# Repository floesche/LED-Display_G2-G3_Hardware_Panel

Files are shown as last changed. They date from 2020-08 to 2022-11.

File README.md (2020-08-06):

---
title: Hardware
parent: Generation 2
---

This repository is related to the Panels project.  It includes the PCB design files, BOM, and datasheets for the (Gen-2) 8x8 LED Panels.

## Project content

```
├── fab_v1p3
└── pcb
    ├── datasheets
    ├── gerber_v1p0
    ├── gerber_v1p1
    ├── gerber_v1p2
    ├── gerber_v1p3
    ├── libs
    ├── mods
    └── old_bom
```

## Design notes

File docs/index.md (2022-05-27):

---
title: Panel
parent: Generation 2
nav_order: 3
---

# Panel 8x8 32mm

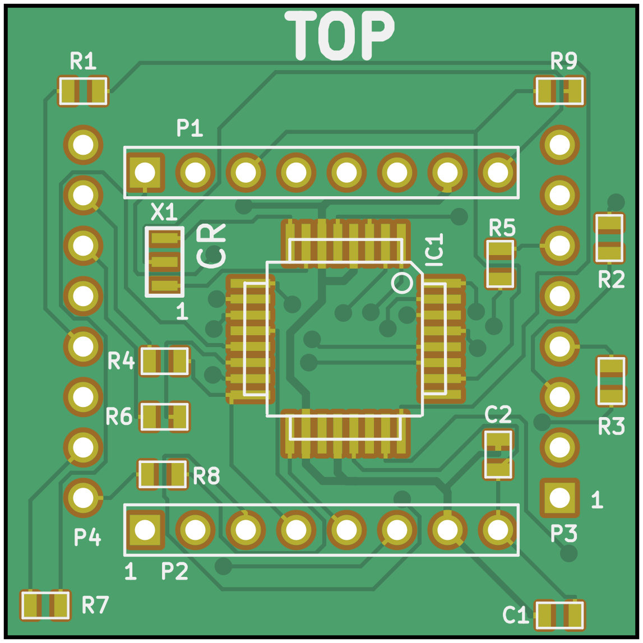
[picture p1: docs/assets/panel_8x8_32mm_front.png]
Panel PCB front view

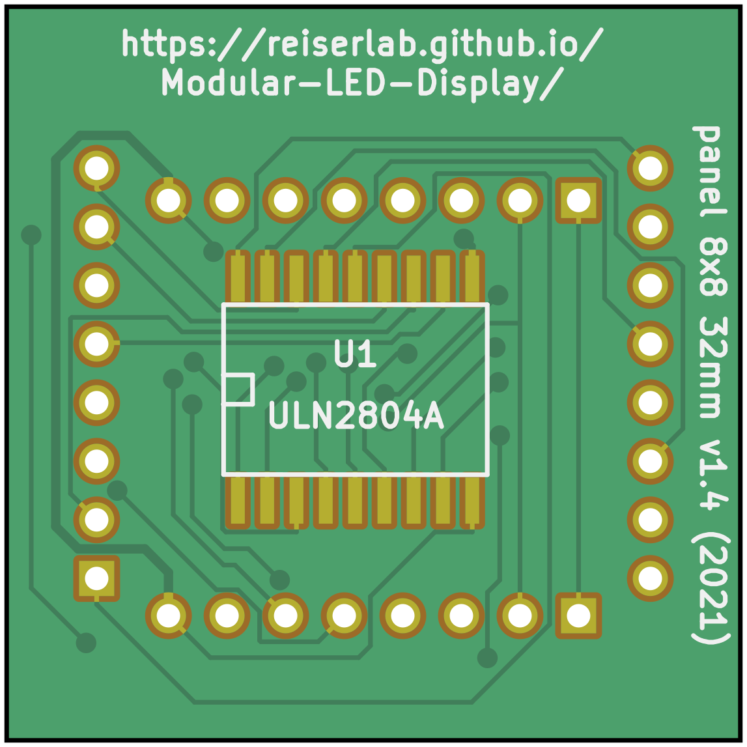
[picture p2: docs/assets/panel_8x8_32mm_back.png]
Panel PCB back view


The display devices in [Generation 2 (G2)]({{site.baseurl}}/G2/) and [Generation 3 (G3)]({{site.baseurl}}/G3/) of the Modular LED Display consists of a standard 8×8 LED matrix component mounted to a custom PCB. This custom PCB, in the original [paper](https://doi.org/10.1016/j.jneumeth.2007.07.019) and our [documentation]({{site.baseurl}}) referred to as the __panel__, is responsible for the communication with the controller. Each panel is individually addressed and communicates with the controller over the TWI bus. Each panel runs a small program which receives updated pattern information and refreshes the display.

__Note__: To clarify the terminology: in [Generation 4]({{site.baseurl}}/G4/) of the Modular LED Display, we built our own LED PCBs (then referred to as [_driver_]({{site.baseurl}}/Generation%204/Panel/docs/driver.html)), and the PCBs providing part of the panel board functionally being called [_comm board_]({{site.baseurl}}/Generation%204/Hardware/docs/comm.html).

## Components

The display devices are a small package that contains a panel board with a microprocessor and line driver, and an 8×8 LED dot matrix display. A brief overview of a [parts list](#parts-list) and the initial sketch of the [schematics](assets/panel_schematic_v2p1.pdf) and [board layout](assets/panel_pcb_v2p1.pdf) are archived here, but when in question always refer to the design and production files as they are more up to date. Each Panel contains an Atmel ATmega8 microcontroller. If you plan to program the Atmel chip, it is a good idea to read the ATmega8 spec sheet. The other chip on the circuit board is an 8-channel darlington driver which acts as a current sink. Current is sourced from the ATmega8's outputs and then passes through a current limiting resistor and one column of the 8×8 LED display. An individual LED is turned on only if the corresponding row line is enabled on the 8-channel current sink, allowing current to flow. In this way it is possible to scan the entire 8×8 array and thus 64 LEDs can be individually controlled with 16 lines. Of course, for this to happen no more than 1 row of LEDs can actually be on at any one time, and so the LEDs must be scanned quickly to prevent the perception of flicker. Currently the entire display is refreshed at 4kHz, and every LED that is on, is only on 12.5% of the time.

The LED matrix component [BM-10288MD](assets/datasheets/BM-10288MD.pdf) (or the alternative [BL-M12A811](assets/datasheets/BL-M12A881.pdf)) that was used in the Generation 2 displays measures 32×32mm² and consists of 8×8 = 64 LEDs. The panel board has the same dimension and is attached to the back of the matrix component. It contains an ATmega168-A and a ULN2804A to drive the LED matrix.

## Design and Production

The KiCad design files are in the `panel_8x8_32mm` directory. Gerber files and a Bill of Materials (BOM) are in a subdirectory `production_v1`. Data sheets for the components used in the built are archived in the `datasheets` directory. For historic reason and although completely outdated we also share the initial [cost estimation](assets/panel_8x8_32mm_costs.xls) done in 2011.

The most recent production of panels we are aware of was in 2020 (please [let us know]({{site.baseurl}}/Contact) if you built another batch). The [Frye lab](https://sites.lifesci.ucla.edu/ibp-frye/research/) used our files version 1.3 (generated in 2012) to order at [Bittele Electronics Inc](https://7pcb.com) in Canada. If you want to replicate the exact same order, feel free to include the order reference number Q12295E in your conversation with Bittele. The panels look a little different from the images above and used the name __flypanel__ internally. The exact same files used in this order are archived at `panel_8x8_32mm/production_v1/panel_8x8_32mm_v1p3.zip`.

The `panel_8x8_32mm/production_v1/panel_8x8_32mm_v1p4.zip` contains a more current, but untested update to the panel. If you are brave enough to order them and have experiences with it, then please get it [contact]({{site.baseurl}}/Contact).

## Software

__Note__: The following sections are out of date. Unless you need to repair a Generation 2 system, follow the instruction in the [Generation 3]({{site.baseurl}}/G3/) menu.
{:.warning}

The software running on each Panel's ATmega8 microcontroller is written in C code, and compiled using the GCC tools for the AVR (WinAVR distribution). Packets are sent to each panel over the TWI bus, the TWI unit on the ATmega8 will only accept a packet if it is addressed either with a 0 (general call) or the address of the panel. In this way specific panels can be targeted. The EEPROM of the ATmega8 is loaded with some patterns, so that the SRAM on the chip is available for pattern buffers. The EEPROM contains the character library for 0…9 and the patterns for the error codes. The EEPROM also has one byte designated for the panel ID, this is set to 0 during the programming.

### Support for Gray Scale (Green Scale)

Multiple levels of //greenscale// patterns are supported by the panels. This is accomplished by further dividing the 4kHz refresh of the panels into either 3 or 7 pieces. When divided into 3 time segments, 4 greenscale levels are possible -- that is each LED can be on for 0, 1, 2, or 3 of the 3 possible time slices. Similarly, when divided into 7 time segments, 8 greenscale levels are possible - each LED can be on for 0,1,…,7 of the 7 total time slices. When measured with a photometer, this scheme is remarkably linear, e.g. the luminance measured for greenlevel 6 is almost exactly 3 times the luminance measured for greenlevel 2. This does reduce the minimum refresh rate to about 570Hz for the 7 levels (so-called `Gray_Scale = 7`), and to about 1333Hz for the 3 levels (so-called `Gray_Scale = 3`). The simplest implementation of this would use 7 copies of the 64-bit pattern map, each bit specifying whether each LED should be on during each time slice. However, we take advantage of binary decoding -- so we need twice the bits -- 16 bytes for each pattern frame at `Gray_Scale = 3`, and 24 bytes for each panels piece of a `Gray_Scale = 7` pattern. The actual way this is done is just a lot of messy, uninteresting boolean algebra. Please read the code if you are interested.

### Panel Address

The address of each panel can be any integer from 1…127. The 0 address is reserved for a general call -- all panels receive packets sent to address 0. The address displays when the panels turn on (and after a reset). Also immediately after a rest or power on, the panels enter a 0.5 second pause, and will be unresponsive to commands and patterns. Only two characters are shown (00…99), and if the value is above 100, the top row of the panel is also  illuminated. It is necessary to give the panels addresses in an incremental manner. If 5 panels, all with address 0 are connected to the controller, and a change address command is issued, all panels with the same address will respond. Read the user guide for instructions on addressing panels.

## Programming the Panels

Because each panel has a microprocessor on-board, each panel needs to be programmed individually. The programming interface (or ISP, in system programming) lines only connect to the microprocessor when the panel is in the left-most position of the controller board, or the plug on the case-mount portion of the controller PCB. The procedure described here is for programming G2 panels (the fuse setting are different for G3 panels). In some eventual future, programming will be done directly from the MATLAB interface. As of right now the procedure is as follows:

1. Once the panel is in place, connect the programming device to the 6 pin header, labelled __Panel ISP__.
2. Open AVR Studio and start the AVR programming tool _STK500/AVRISP_{:.gui-btn} from the tools menu.
3. Test the connection by selecting the ATmega8 device from the drop-down menu, and then in the advanced tab try to read signature. If these match, move on, otherwise check the connections, restart, etc.
4. Program the fuses. This is done from the _Fuses_{:.gui-btn} tab – these options should be set: _Preserve EEPROM memory through chip erase cycle_{:.gui-txt} to _on_{:.gui-txt}, and set clock rate to the last choice: _Ext. Crystal/Resonator High Freq._{:.gui-txt}: _Start-up time 16K CK + 64 ms_{:.gui-txt}. It is also a good idea to set _Brown-out detection level at VCC_{:.gui-txt} = _4.0V_{:.gui-txt} and _Brown-out detection enabled_{:.gui-txt}.
5. Program the EEPROM on the Atmega8 by selecting the _Program_{:.gui-btn} tab and electing the input hex file as: _panel.eep_{:.gui-txt}, and then programming the chip.
6. Program the flash on the Atmega8 by selecting the _Program_{:.gui-btn} tab and selecting the input hex file as: _panel.hex_{:.gui-txt}, and then programming the chip.
7. If this is all done correctly the LED should display 00 and the display should be bright with no flicker. If it appears dull or flickery - the clock was probably not set correctly. It is always a good idea to verify both the program and the fuses to make sure these are set correctly.

For programming many panels this process can be automated by using the _Auto_{:.gui-btn} tab and selecting _program FLASH_{:.gui-txt}, _program EEPROM_{:.gui-txt}, and _program fuses_{:.gui-txt}. Once a panel is programmed it needs to be addressed, this is done using the PControl software.

# Parts list {#parts-list}

| quantity | part description               | source & p/n | price |
|---------:|:-------------------------------|:-------------|------:|
| 1        | 8×8 green [LED display]({{site.baseurl}}/Generation%203/Hardware/docs/assets/green-panels_BM-10288MD.pdf) | American Bright, BM-10288MI | $2.50 |
| 1        | 8 Pin rt angle male header              | Major League, LTSHR-108-S-02-A-T | $0.23 |
| 1        | 8 Pin rt angle fem. header              | Major League, SSHR-108-S-02-L-T | $0.38 |
| 8        | 82Ohm resistor, 1/10W, 1%, 0603 package | Digi-Key, 311-82.0HTR-ND | $0.005 |
| 1        | 1kOhm resistor, 1/10W, 5%, 0603 package | Digi-Key, 311-10KGCT-ND | $0.02 |
| 1        | 0.33µF capacitor, ceramic, 1206 package | Digi-Key, PCC1889CT-ND | $0.09 |
| 1        | 16MHz ceramic resonator w. capacitors   | Digi-Key, X908-ND | $0.30 |
| 1        | 8 CH line driver ULN2804A 8-SOL package | Digi-Key, ULN2804AFW-ND | $0.35 |
| 1        | [Atmega8](http://www.atmel.com/dyn/resources/prod_documents/doc2486.pdf) microcontroller, 32 TQFP package| Digi-Key, ATMEGA8-16AI-ND | $2.25 |
| 1        | Panel PCB                               | ordered from Advanced Circuits | |

__Optional__: 2 8-Pin straight female headers, Jameco p/n 70754 ($0.23), can be used so that the LED displays are socketed, this is convenient, but also will not guarantee ideal contact between circuit and display.

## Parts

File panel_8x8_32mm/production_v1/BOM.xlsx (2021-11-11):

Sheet: Sheet1
Item# | Qty | References | part desc. | mfg P/N | vendor | price | $100 | $500 | $1000 | $1500 | $2000 | 100 | 500 | 1000 | 1500 | 2000 | price/board_100 | price/board_500 | price/board_1000 | price/board_1500 | price/board_2000 | MOQ | Availability | Comments_Lj | Your Comments
1 | 1 | U1 | IC DRIVER DARL 8CH 50V.5A 18-SO | ULN2804AFWG(CELHACT-ND) | Digikey | 0.92 | 0.63 | 0.462 | 0.3675 | 0.336 | 0.3045 | 100 | 500 | 1000 | 1500 | 2000 | 0.63 | 0.462 | 0.3675 | 0.336 | 0.3045 | 1 | 26688
2 | 1 | IC1 | IC AVR MCU 16K 20MHZ 32TQFP | ATMEGA168-20AU-ND | Digikey | 4.32 | 2.412 | 2.412 | 2.412 | 2.412 | 2.412 | 100 | 500 | 1000 | 1500 | 2000 | 2.412 | 2.412 | 2.412 | 2.412 | 2.412 | 1 | 53937
3 | 2 | P3, P4 | 8 POS PEEL-A-WAY SIP CONN. | Custom | Adv. Interconn. |  |  |  |  |  |  |  |  |  | 3000 | 4000 | 0 | 0 | 0 | 0 | 0 |  |  |  | Already purchased. This is a 32 position strip. The board requires 2x8 pos strips.
4 | 8 | R1, R2, R3, R4, R5, R6, R7, R8 | RES 0603 82 OHM 1/10W 1% | P82.0HCT-ND | Digikey | 0.8 | 0.0105 | 0.00576 | 0.00384 | 0.00198 | 0.00198 | 800 | 4000 | 8000 | 12000 | 16000 | 0.084 | 0.04608 | 0.03072 | 0.01584 | 0.01584 | 1 | 77007
5 | 1 | R9 | RES 0603 10K OHM 1/10W 5% | P10KGCT-ND | Digikey | 0.1 | 0.007 | 0.00384 | 0.00256 | 0.00256 | 0.00256 | 100 | 500 | 1000 | 1500 | 2000 | 0.007 | 0.00384 | 0.00256 | 0.00256 | 0.00256 | 1 | 13551465
6 | 2 | C1, C2 | CAP 0603 0.33 uF | PCC2274CT-ND | Digikey | 0.5 | 0.0573 | 0.0293 | 0.0207 | 0.0172 | 0.0172 | 200 | 1000 | 2000 | 3000 | 4000 | 0.1146 | 0.0586 | 0.0414 | 0.0344 | 0.0344 | 1 | 138896 | No stock available with major suppliers. Please provide an alternate p/n. | Providing alternative part number. Please purchase the 4,000 MOQ and keep the surplus in stock. We will be placing recurring orders.
7 | 1 | P2 | CONN RIGHT-ANGLE, 8 POS, MALE | LTSHR-108-S-02-A-T | MLE |  |  |  |  |  |  |  |  | 1000 | 1500 | 2000 | 0 | 0 | 0 | 0 | 0 |  |  |  | Already purchased
8 | 1 | P1 | CONN RIGHT-ANGLE, 8 POS, FEMALE | SSHR-108-S-02-L-T | MLE |  |  |  |  |  |  |  |  | 1000 | 1500 | 2000 | 0 | 0 | 0 | 0 | 0 |  |  |  | Already purchased
9 | 1 | X1 | CERAMIC RES 20 MHz | 490-1199-6-ND | Digikey | 0.95 | 0.4731 | 0.35862 | 0.32809 | 0.25637 | 0.25637 | 100 | 500 | 1000 | 1500 | 2000 | 0.4731 | 0.35862 | 0.32809 | 0.25637 | 0.25637 | 1 | 34790
 |  |  |  |  |  |  |  |  |  |  |  |  |  |  |  |  | 3.7207 | 3.34114 | 3.18227 | 3.05717 | 3.02567
 |  |  |  |  |  |  |  |  |  |  |  |  |  |  |  |  | 0.186035 | 0.167057 | 0.1591135 | 0.1528585 | 0.1512835
 |  |  |  |  |  |  |  |  |  |  |  |  |  |  |  |  | 1.1 | 0.38 | 0.31 | 0.2333333333 | 0.195
 |  |  |  |  |  |  |  |  |  |  |  |  |  |  |  |  | 0.18 | 0.036 | 0.018 | 0.012 | 0.009
 |  |  |  |  |  |  |  |  |  |  |  |  |  |  |  | Total: | 5.186735 | 3.924197 | 3.6693835 | 3.455361833 | 3.3809535

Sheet: BOM_SS
Item# | Qty | References | part desc. | mfg P/N | vendor
1 | 1 | U1 | IC DRIVER DARL 8CH 50V.5A 18-SO | ULN2804AFWG(CELHACT-ND) | Digikey
2 | 1 | IC1 | IC AVR MCU 16K 20MHZ 32TQFP | ATMEGA168-20AU-ND | Digikey
3 | 16 | P3, P4 | PIN RECEPTACLES | Elpacko PN 4007-2-01-32-12 | Straight Road Electronics ( see * below)
4 | 8 | R1, R2, R3, R4, R5, R6, R7, R8 | RES 0603 82 OHM 1/10W 1% | P82.0HCT-ND | Digikey
5 | 1 | R9 | RES 0603 10K OHM 1/10W 5% | P10KGCT-ND | Digikey
6 | 2 | C1, C2 | CAP 0603 0.33 uF | 445-12434-1-ND | Digikey
7 | 1 | P2 | CONN RIGHT-ANGLE, 8 POS, MALE | S1111EC-08-ND | Digikey
8 | 1 | P1 | CONN RIGHT-ANGLE, 8 POS, FEMALE | SAM1195-08-ND | Digikey
9 | 1 | X1 | CERAMIC RES 20 MHz | 490-1199-6-ND | Digikey
* Supplied by Straight Road electronics http://www.straightroadelectronics.com/ Contact: Debby Arrin (949) 215-9449.

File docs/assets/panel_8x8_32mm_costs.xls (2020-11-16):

2012-09-15 IO Rodeo Inc.
Flypanels cost matrix (v1.0)
Option 1: Green LED Matrix (similar spectrum to American Bright)
Qty. | PCB | LED (G) | Sub-Total | Shipping | Sub-Total2 | 50% | 60% | 100% | % ($2.50)
100 | 16.84 | 1.678 | 18.52 | 0.50 | 19.02 | 28.53 | 30.43 | 38.04 | 6.6
500 | 10.71 | 1.678 | 12.39 | 0.13 | 12.52 | 18.78 | 20.03 | 25.04 | 10.0
1000 | 9.18 | 1.678 | 10.86 | 0.08 | 10.94 | 16.41 | 17.50 | 21.88 | 11.4
Option 2: Ultra-Green LED Matrix (broader spectrum to American Bright)
Qty. | PCB | LED (UG) | Sub-Total | Shipping | Sub-Total2 | 50% | 60% | 100% | % ($2.50)
100 | 16.84 | 1.968 | 18.81 | 0.50 | 19.31 | 28.96 | 30.89 | 38.62 | 6.5
500 | 10.71 | 1.968 | 12.68 | 0.13 | 12.81 | 19.21 | 20.49 | 25.62 | 9.8
1000 | 9.18 | 1.968 | 11.15 | 0.08 | 11.23 | 16.84 | 17.96 | 22.46 | 11.1

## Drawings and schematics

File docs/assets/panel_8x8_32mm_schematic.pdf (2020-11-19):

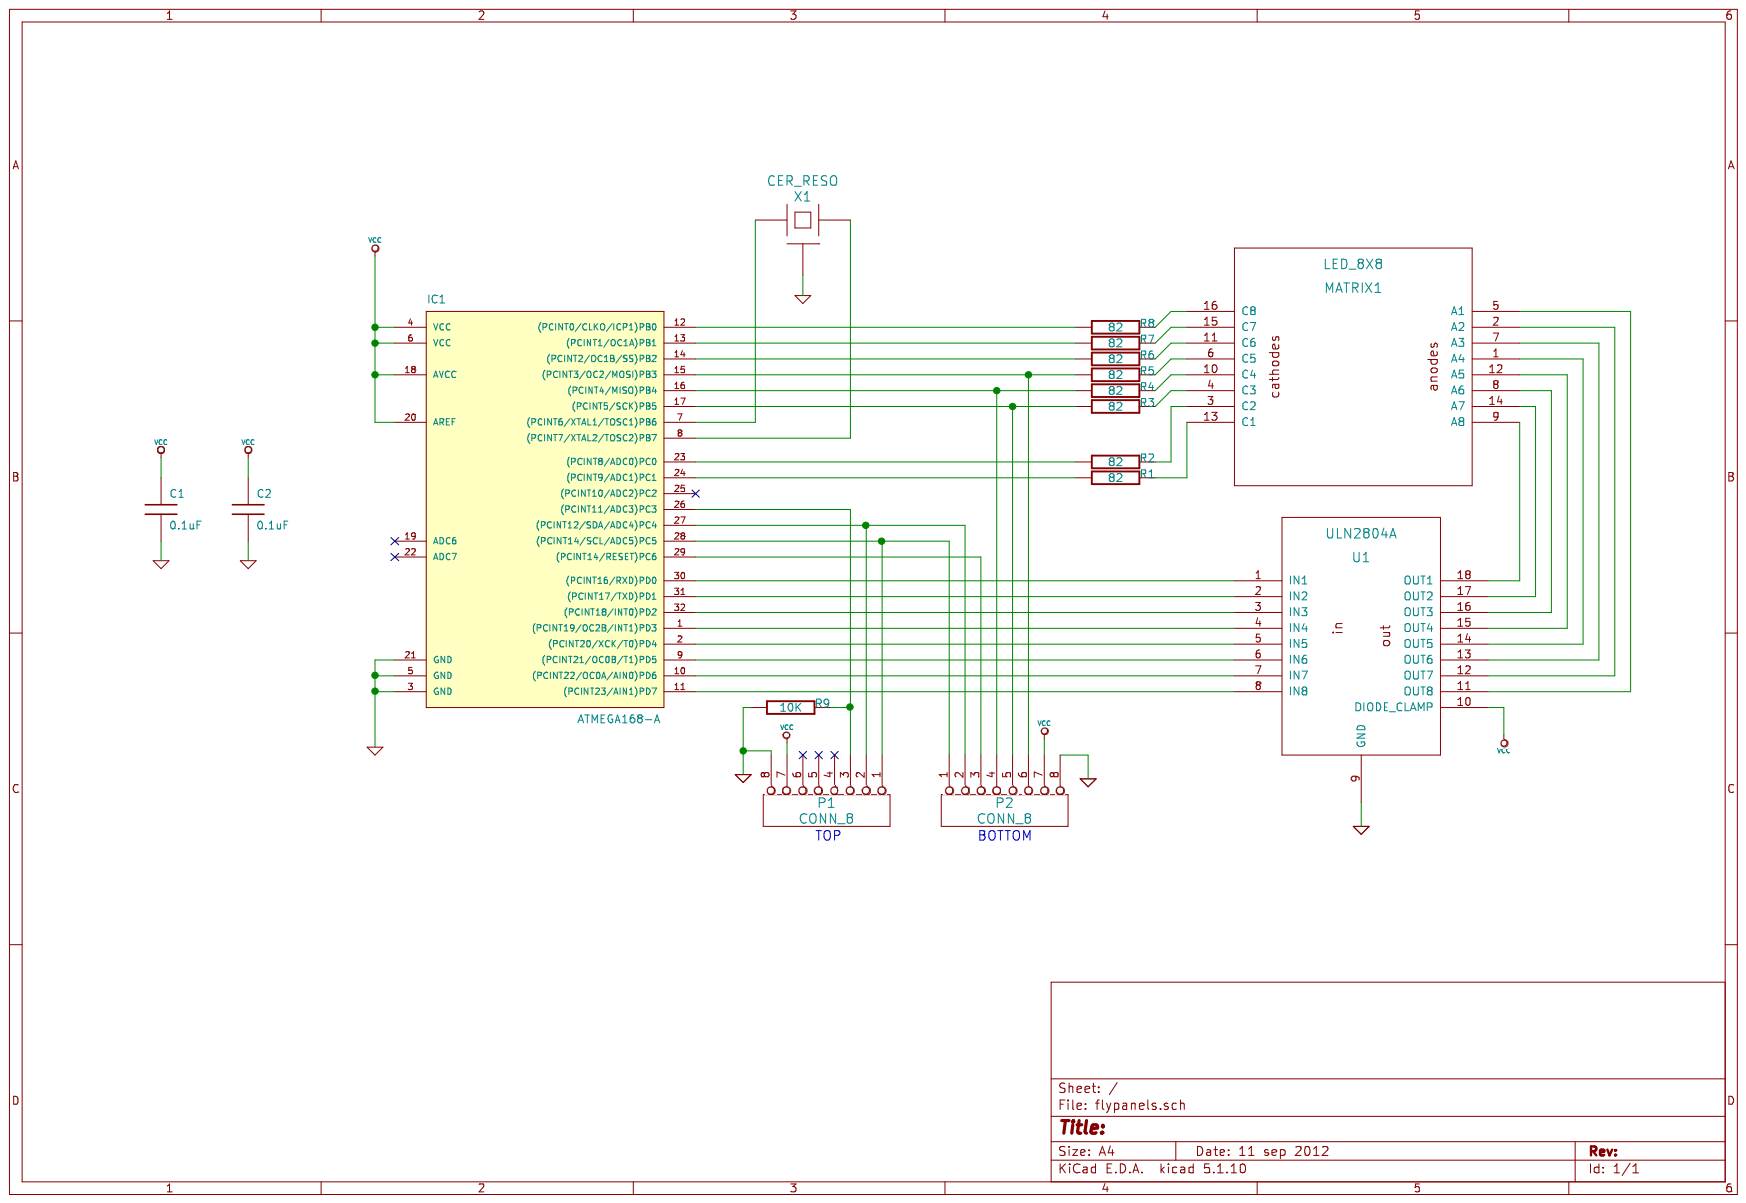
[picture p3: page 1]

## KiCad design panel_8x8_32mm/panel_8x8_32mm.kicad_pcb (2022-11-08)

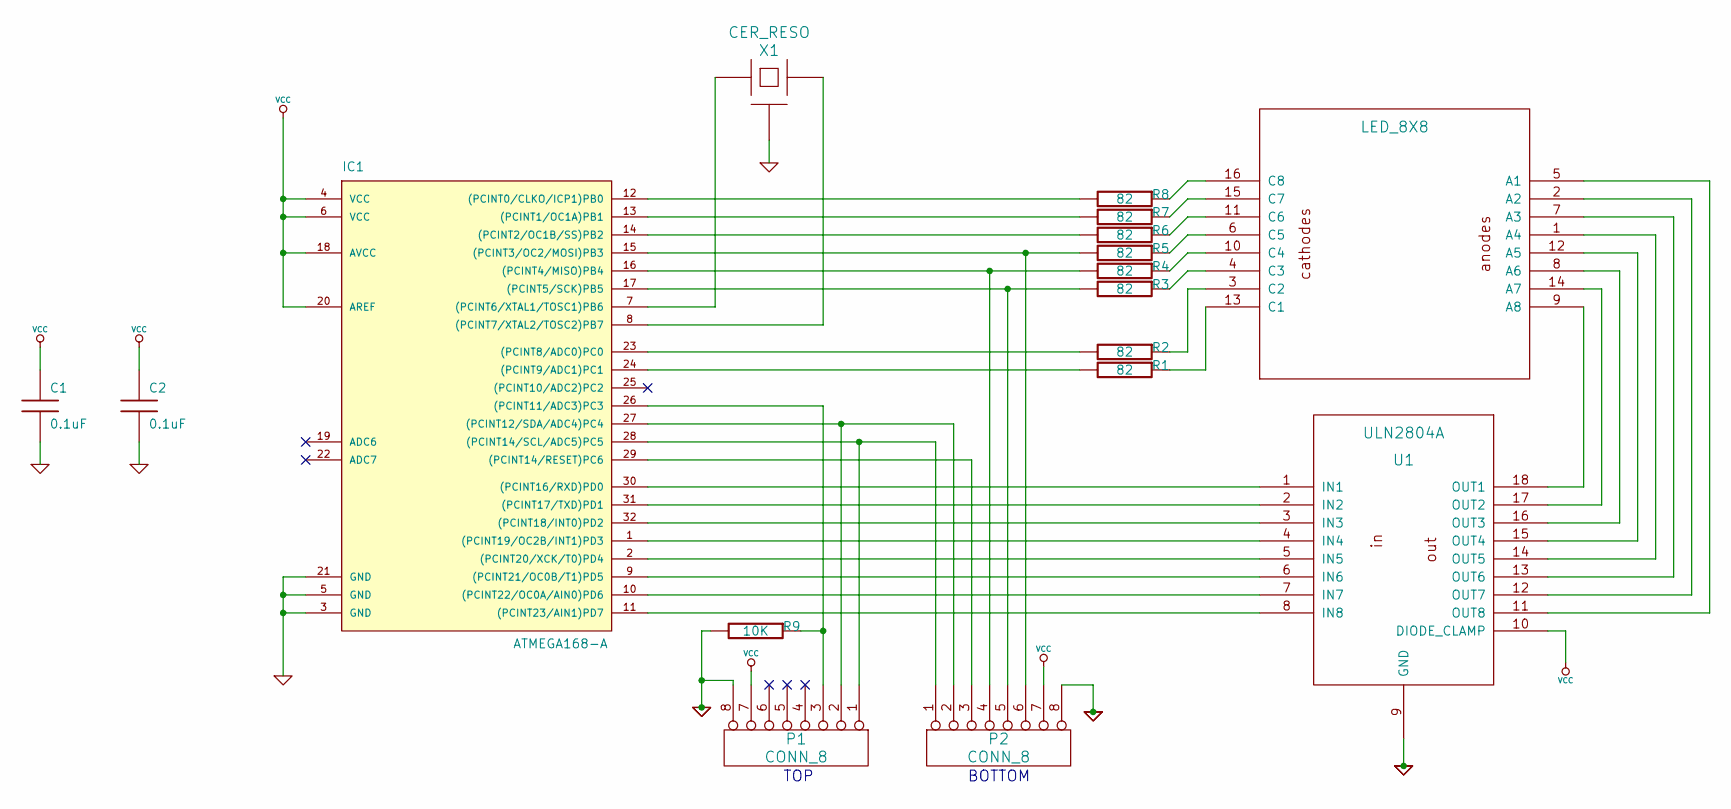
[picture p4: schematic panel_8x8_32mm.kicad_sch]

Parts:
C1, C2: 0.1uF
IC1: ATMEGA168-A; TQFP32
P1, P2: CONN_8
R1, R2, R3, R4, R5, R6, R7, R8: 82
R9: 10K
U1: ULN2804A
X1: CER_RESO

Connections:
GND: C1.2, C2.2, IC1.3 (GND), IC1.5 (GND), IC1.21 (GND), P1.8, P2.8, R9.2, U1.9 (GND), X1.2 (GND)
unnamed 1: R2.1; also elsewhere on the board
unnamed: IC1.28 ((PCINT14/SCL/ADC5)PC5), P1.1, P2.1
unnamed 3: U1.14 (OUT5); also elsewhere on the board
unnamed 4: U1.16 (OUT3); also elsewhere on the board
unnamed: IC1.27 ((PCINT12/SDA/ADC4)PC4), P1.2, P2.2
unnamed: IC1.16 ((PCINT4/MISO)PB4), P2.4, R4.2
unnamed: IC1.15 ((PCINT3/OC2/MOSI)PB3), P2.6, R5.2
unnamed: IC1.2 ((PCINT20/XCK/T0)PD4), U1.5 (IN5)
unnamed: IC1.8 ((PCINT7/XTAL2/TOSC2)PB7), X1.3
unnamed: IC1.9 ((PCINT21/OC0B/T1)PD5), U1.6 (IN6)
unnamed: IC1.10 ((PCINT22/OC0A/AIN0)PD6), U1.7 (IN7)
unnamed: IC1.30 ((PCINT16/RXD)PD0), U1.1 (IN1)
unnamed: IC1.11 ((PCINT23/AIN1)PD7), U1.8 (IN8)
unnamed: IC1.31 ((PCINT17/TXD)PD1), U1.2 (IN2)
unnamed: IC1.12 ((PCINT0/CLKO/ICP1)PB0), R8.2
unnamed: IC1.1 ((PCINT19/OC2B/INT1)PD3), U1.4 (IN4)
unnamed: IC1.32 ((PCINT18/INT0)PD2), U1.3 (IN3)
unnamed: IC1.23 ((PCINT8/ADC0)PC0), R2.2
unnamed: IC1.24 ((PCINT9/ADC1)PC1), R1.2
unnamed: IC1.26 ((PCINT11/ADC3)PC3), P1.3, R9.1
unnamed: IC1.29 ((PCINT14/RESET)PC6), P2.3
unnamed 22: U1.11 (OUT8); also elsewhere on the board
unnamed 23: U1.18 (OUT1); also elsewhere on the board
unnamed: IC1.14 ((PCINT2/OC1B/SS)PB2), R6.2
unnamed 25: R5.1; also elsewhere on the board
unnamed: IC1.13 ((PCINT1/OC1A)PB1), R7.2
unnamed 27: R3.1; also elsewhere on the board
unnamed 28: U1.13 (OUT6); also elsewhere on the board
unnamed 29: R4.1; also elsewhere on the board
unnamed 30: R6.1; also elsewhere on the board
unnamed 31: U1.15 (OUT4); also elsewhere on the board
unnamed 32: R1.1; also elsewhere on the board
unnamed 33: U1.17 (OUT2); also elsewhere on the board
unnamed 34: R7.1; also elsewhere on the board
unnamed 35: R8.1; also elsewhere on the board
unnamed 36: U1.12 (OUT7); also elsewhere on the board
unnamed: IC1.7 ((PCINT6/XTAL1/TOSC1)PB6), X1.1
unnamed: IC1.17 ((PCINT5/SCK)PB5), P2.5, R3.2
VCC: C1.1, C2.1, IC1.4 (VCC), IC1.6 (VCC), IC1.18 (AVCC), IC1.20 (AREF), P1.7, P2.7, U1.10 (DIODE_CLAMP)

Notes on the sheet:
TOP
BOTTOM

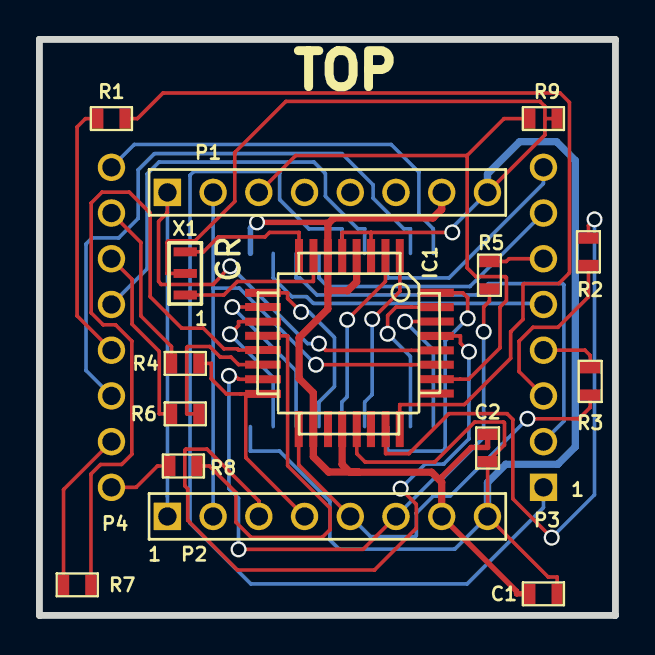
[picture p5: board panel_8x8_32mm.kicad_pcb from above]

Board: 2 copper layers, 32.0 x 32.0 mm, 17 parts (1 on the bottom side), 40 nets.

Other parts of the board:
MATRIX1: LED_8X8; LED_8x8

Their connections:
unnamed 1: MATRIX1.3; also elsewhere on the board
unnamed 3: MATRIX1.1; also elsewhere on the board
unnamed 4: MATRIX1.8; also elsewhere on the board
unnamed 22: MATRIX1.5; also elsewhere on the board
unnamed 23: MATRIX1.9; also elsewhere on the board
unnamed 25: MATRIX1.6; also elsewhere on the board
unnamed 27: MATRIX1.4; also elsewhere on the board
unnamed 28: MATRIX1.7; also elsewhere on the board
unnamed 29: MATRIX1.10; also elsewhere on the board
unnamed 30: MATRIX1.11; also elsewhere on the board
unnamed 31: MATRIX1.12; also elsewhere on the board
unnamed 32: MATRIX1.13; also elsewhere on the board
unnamed 33: MATRIX1.14; also elsewhere on the board
unnamed 34: MATRIX1.15; also elsewhere on the board
unnamed 35: MATRIX1.16; also elsewhere on the board
unnamed 36: MATRIX1.2; also elsewhere on the board

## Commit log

2020-11-16 restructure repository
    [$savepcb.brd, 12295_V03_BOM.xls, flypanels-Back.gbl, flypanels-Front.gtl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]
2020-11-18 file cleanup
    [$savepcb.brd, flypanels.brd, flypanels.kicad_pcb]
2021-11-11 consistent file naming
    [BOM.xlsx, flypanels.dsn, flypanels_BOM.xls, panel_8x8_32mm-B_Mask.gbs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]
2022-11-08 migrate to KiCad 6
    [panel_8x8_32mm.kicad_pcb, panel_8x8_32mm.kicad_sch, panel_8x8_32mm.sch]
